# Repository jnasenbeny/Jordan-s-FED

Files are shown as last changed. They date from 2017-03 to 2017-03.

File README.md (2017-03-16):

# Jordan-s-FED
Based on the original FED from Kravitz Lab, this user-friendly device is designed to reliably dispense 45 mg rodent food pellets with minimal tinkering. A number of changes, described below, were made to the physical structure of the device. Two 'for loops' were added to the code, causing the direction of motor rotation to alternate after either 1) successful pellet dispense or 2) twelve motor steps without successful pellet dispense.  Alternating motor direction alleviates clogs in the silo.  

----------------------------------------------------------------------------------------------------------------------------------------

3D Print Design Changes from original FED are summarized as follows:

Silo:
Pellets are swept single file underneath an oval shaped wall, alleviating strain which caused clogging in the original model. Clogging is greatly reduced, increasing reliability of successful pellet dispenses and extending battery life. 

Disk:
Pellet holes widened and deepened to accomodate one 45 mg pellet at a time. 

Motor mount:
Disk tray deepened to accomodate the now taller disk.

Funnel:
Instead of dropping vertically, pellets now tumble down an ovaloid chute which sweeps laterally, reducing the chance of pellets bouncing out of the well. The new funnel piece is wider than the original and snaps into place without the use of screws.

Base:
(1) Standouts for PCB machine screws were rotated 90 degrees to make the device more user friendly. Now, the SD card is easily reached. The Power Booster lies flat on the floor and battery charging is done with the device standing upright. This increases user friendliness and slightly increases the size of the device. 
(2) Designated battery slot added to improve organization. 
(3) Switch slot was moved from the side of the device to the top, more efficiently using vertical space. 
(4) Pellet ramp was narrowed with the simple addition of walls. Pellets fall through an oval hole instead of a square one. 

Front Plate:
This component was removed from the design, since the funnel piece accomplishes the job of the old front plate. 

Lid and Back Panel:
No changes.

----------------------------------------------------------------------------------------------------------------------------------------

Performance Results:

I built 5 FEDs with these new pieces. The silos were filled completely with 45 mg pellets, and then 150 consecutive dispensing events and errors were recorded. A success counts as a single pellet landing in the well. Errors were of two types: 1) pellet bouncing out of the well; 2) two pellets dropping into the well at once. Mean success rate = 98.8%, median success rate = 98.7%.

Device 1: 
Successes -- 148/150, Errors -- bounce outs, 2.

Device 2: 
Successes -- 150/150, Errors -- none.

Device 3: 
Successes -- 149/150, Errors -- bounce out, 1.

Device 4: 
Successes -- 148/150, Errors -- bounce out, 1. double drop, 1.

Device 5:
Successes -- 148/150, Errors -- bounce out, 1. double drop, 1.

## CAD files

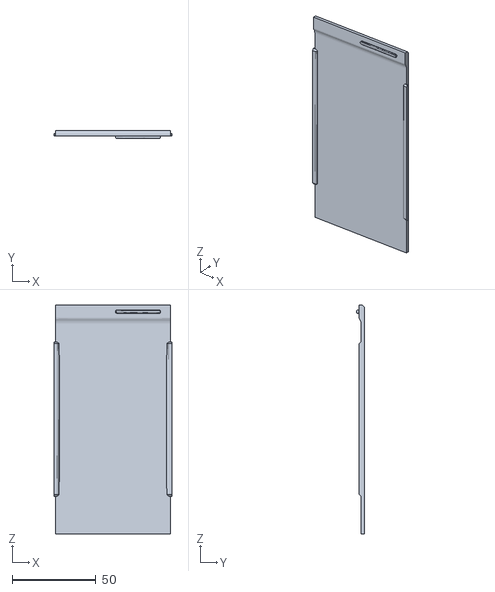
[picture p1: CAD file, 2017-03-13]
Original FED back cover.stl
70.5 x 4.75 x 137.0

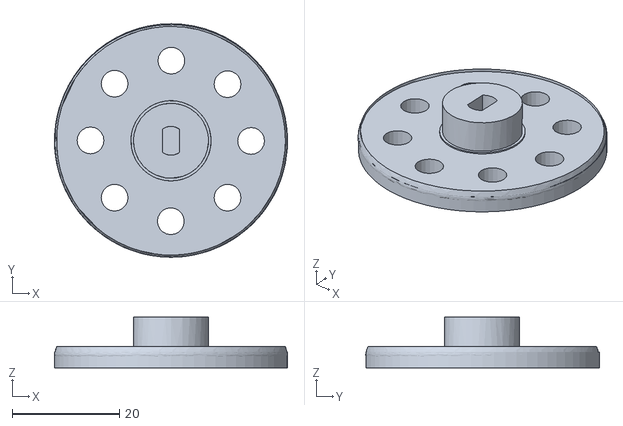
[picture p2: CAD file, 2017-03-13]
Jordan's 45 mg pellet disk.stl
43.5 x 43.6 x 9.50

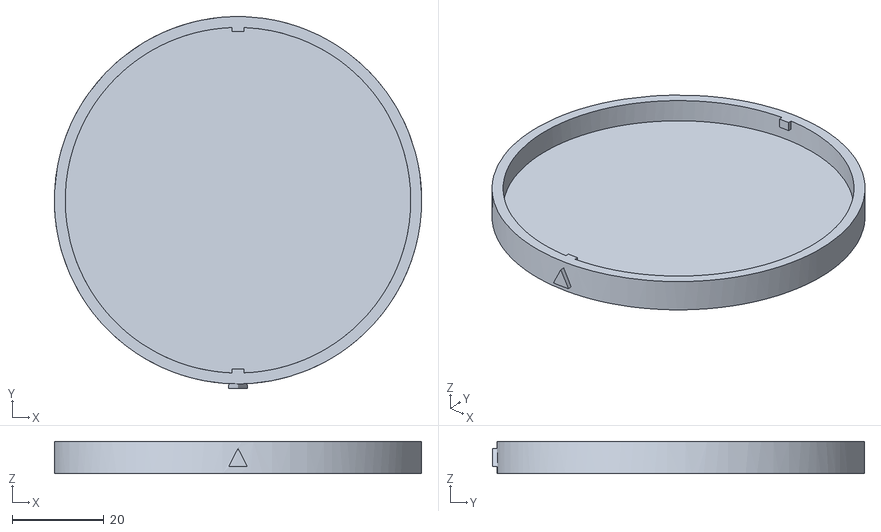
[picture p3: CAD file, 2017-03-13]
Original FED pellet hopper lid.stl
80.0 x 81.0 x 7.00

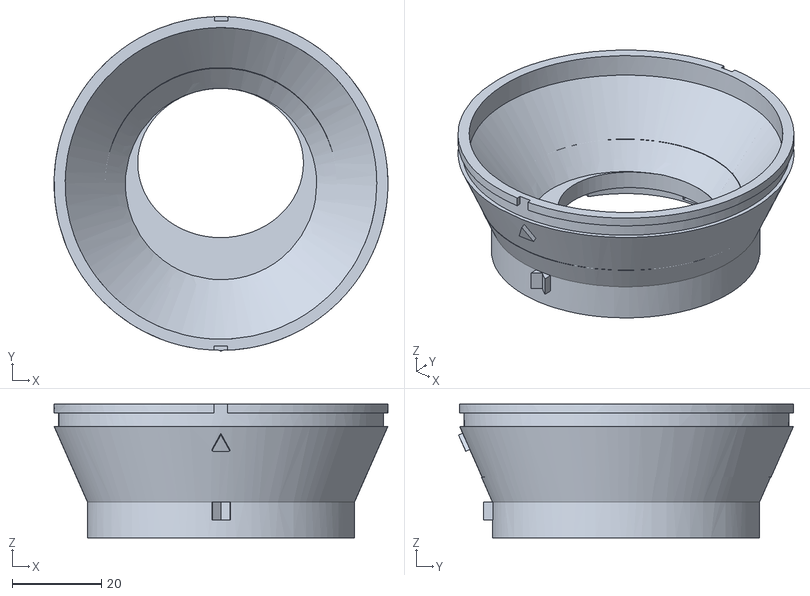
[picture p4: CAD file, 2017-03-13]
Jordan's Silo.stl
75.0 x 75.2 x 30.0

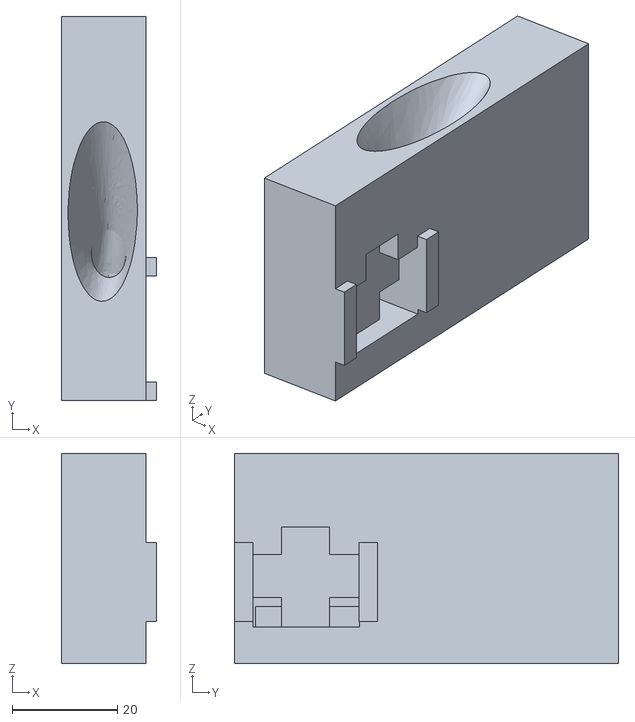
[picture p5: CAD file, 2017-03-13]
Jordan's funnel.stl
18.0 x 73.0 x 40.0

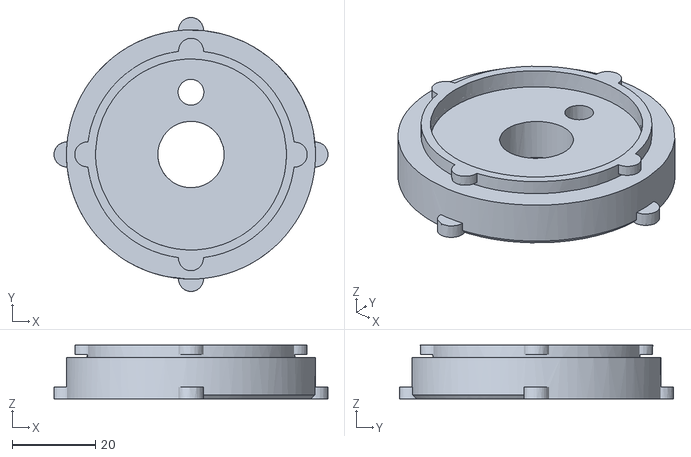
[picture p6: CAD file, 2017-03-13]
Jordan's motor mount.stl
66.0 x 66.0 x 13.0

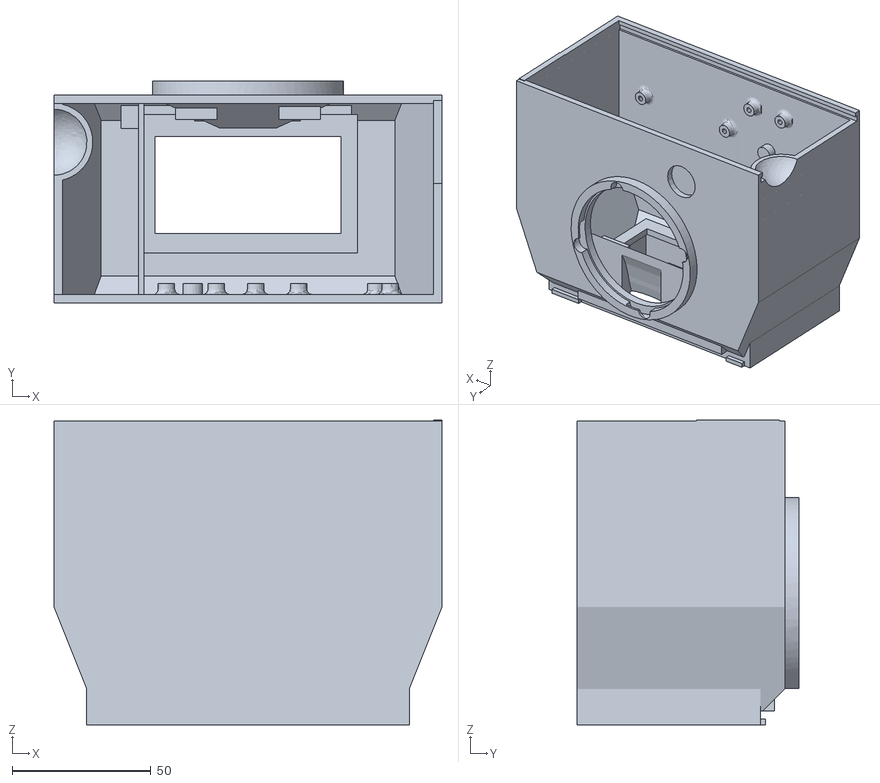
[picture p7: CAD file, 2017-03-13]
Jordan's FED Base.stl
140.0 x 80.0 x 110.0

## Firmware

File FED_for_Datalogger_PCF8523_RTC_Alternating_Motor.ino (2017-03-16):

// use this code for Arduino Data Logger Shields with PCF8523 Real Time Clock.
// Motor is set to alternate direction of rotation according to for loops in lines 168-250


#include <avr/sleep.h>
#include <avr/power.h>
#include <avr/wdt.h>
#include <SdFat.h>                // SD and RTC libraries
#include "RTClib.h"
#include <Wire.h>
#include <Stepper.h>
#include <SPI.h>
#include <Adafruit_GFX.h>
#include <Adafruit_SharpMem.h>
#include <avr/interrupt.h>
#include <avr/io.h>
#include <SoftwareSerial.h>
#include <Adafruit_MotorShield.h>



#define FILENAME "YOUR_FILENAME_HERE.csv"

#define DISPLAY_SERIAL_RX_PIN 255 // we don't need a receive pin, 255 indicates this
// Connect the Arduino pin 3 to the rx pin on the 7 segment display
#define DISPLAY_SERIAL_TX_PIN 9

// Photo interrupter is also the wakeup for the system
#define PHOTO_INTERRUPTER_PIN 2

//initialize the rtc
RTC_PCF8523 rtc;

SoftwareSerial LEDserial = SoftwareSerial(DISPLAY_SERIAL_RX_PIN, DISPLAY_SERIAL_TX_PIN);
SdFat SD;

long previousMillis = 0; 
long startTime = 0;
long timeElapsed = 0;
const long day2 = 86400000; // 86400000 milliseconds in a day
const long hour2 = 3600000; // 3600000 milliseconds in an hour
const long minute2 = 60000; // 60000 milliseconds in a minute
const long second2 =  1000; // 1000 milliseconds in a second

const int CS_pin = 10;

String time;
File dataFile;

const int TTL_DEBUG_PIN = 3;

const int STEPS_TO_INCREMENT = 65;
const int MOTOR_STEPS_PER_REVOLUTION = 513;

int PIState = 1;
int lastState = 1;

int pelletCount = 0;

// Stepper motor with shield test
Adafruit_MotorShield gMotorShield = Adafruit_MotorShield();
// Set the second argument to 1 to use M1 and M2 on the motor shield, or set as 2 to use M3 and M4:
Adafruit_StepperMotor *gPtrToStepper = gMotorShield.getStepper(MOTOR_STEPS_PER_REVOLUTION,1); 

int logData() {
  String year, month, day, hour, minute, second;
  power_twi_enable();
  power_spi_enable();

  DateTime datetime = rtc.now();
  year = String(datetime.year(), DEC);
  month = String(datetime.month(), DEC);
  day  = String(datetime.day(),  DEC);
  hour  = String(datetime.hour(),  DEC);
  minute = String(datetime.minute(), DEC);
  second = String(datetime.second(), DEC);

  // concatenates the strings defined above into date and time
  time = month + "/" + day + " " + hour + ":" + minute + ":" + second;

  // opens a file on the SD card and prints a new line with the
  // current reinforcement schedule, the time stamp,
  // the number of sucrose deliveries, the number of active and
  // inactive pokes, and the number of drinking well entries.

  dataFile = SD.open(FILENAME, FILE_WRITE);
  if (dataFile) {
    Serial.println(F("File successfully written..."));
    Serial.println(time);
    dataFile.print(time);
    dataFile.print(",");
    dataFile.print(pelletCount);
    dataFile.print(",");
    dataFile.println(timeElapsed);
    dataFile.close();
  }
  power_twi_disable();
  power_spi_disable();
}

void setup()
{

  // make all unused pins inputs with pullups enabled by default, lowest power drain
  // leave pins 0 & 1 (Arduino RX and TX) as they are
  for (byte i=2; i <= 20; i++) {    
    pinMode(i, INPUT_PULLUP);     
  }
  ADCSRA = 0;  // disable ADC as we won't be using it
  power_adc_disable(); // ADC converter
  power_timer1_disable();// Timer 1
  power_timer2_disable();// Timer 2

  Serial.begin(9600);
  Serial.println(F("Starting up..."));

  pinMode(PHOTO_INTERRUPTER_PIN, INPUT);
  pinMode(TTL_DEBUG_PIN, OUTPUT);
  pinMode(CS_pin, OUTPUT);
  pinMode(SS, OUTPUT);

  Wire.begin();
  
  // both the stepper control and RTC use I2C (the Wire library)
  rtc.begin(); // RTC library needs Wire

  // set up stepper
  gMotorShield.begin(); // use default I2C address of 0x40
  gPtrToStepper->setSpeed(30); // rpm, max suggested by Adafruit for this 5V stepper

  if (! rtc.initialized()) {
    Serial.println("RTC is NOT running!");
    // following line sets the RTC to the date & time this sketch was compiled
    rtc.adjust(DateTime(F(__DATE__), F(__TIME__)));
    // This line sets the RTC with an explicit date & time, for example to set
    // January 21, 2014 at 3am you would call:
    // rtc.adjust(DateTime(2014, 1, 21, 3, 0, 0));
  }

  if (!SD.begin(CS_pin)) {
    Serial.println(F("Card failed, or not present"));
    // don't do anything more:
    while (1) ;
  }

  Serial.println(F("Card initialized."));

  dataFile = SD.open(FILENAME, FILE_WRITE);
  if (! dataFile) {
    Serial.println(F("Error opening datalog.txt"));
    // Wait forever since we cant write data
    while (1) ;
  }

  else {
    dataFile.print(time);
    dataFile.println(F("Time,Pellet Count,Pellet Drop Delay"));
    dataFile.close();
  }
    
  delay (50);
  
  // get ready for what the system should be doing
  PIState = digitalRead(PHOTO_INTERRUPTER_PIN);
  lastState = 0;
}

void loop()
{
  int i = 0;
  int j = 0;
  
  for (i = 0; i < 12; i++){
  PIState = digitalRead(PHOTO_INTERRUPTER_PIN);
  Serial.print("Photointerrupter State: ");
  Serial.println(PIState);
  digitalWrite(TTL_DEBUG_PIN, LOW);

  if (PIState == 1  & PIState != lastState) {    
    digitalWrite(TTL_DEBUG_PIN, HIGH);    
    startTime = millis();
    Serial.print(F("Time Elapsed Check: "));
    Serial.println(timeElapsed);
    timecounter(timeElapsed);
    pelletCount ++;
    logData();
    Serial.println(F("It did work"));
    lastState = PIState;
  }
  else if (PIState == 1) {
    Serial.println(F("Turning motor..."));
    power_twi_enable();
    gPtrToStepper->step(STEPS_TO_INCREMENT/4,BACKWARD,DOUBLE);
    delay(500);
    if (PIState == 1) {gPtrToStepper->step(STEPS_TO_INCREMENT, FORWARD, DOUBLE);} 
    gPtrToStepper->release();
    power_twi_disable();
    lastState = PIState;
    delay(500);
  }
  
  else if (PIState == 0 & PIState != lastState) {
    Serial.print(F("Time Elapsed Since Last Pellet: "));
    timeElapsed = millis() - startTime;
    Serial.println(timeElapsed);
    lastState = PIState;
    break;
  }
  delay (500);
  }
    for (j = 0; j < 12; j++){
    PIState = digitalRead(PHOTO_INTERRUPTER_PIN);
  Serial.print("Photointerrupter State: ");
  Serial.println(PIState);
  digitalWrite(TTL_DEBUG_PIN, LOW);

  if (PIState == 1  & PIState != lastState) {    
    digitalWrite(TTL_DEBUG_PIN, HIGH);    
    startTime = millis();
    Serial.print(F("Time Elapsed Check: "));
    Serial.println(timeElapsed);
    timecounter(timeElapsed);
    pelletCount ++;
    logData();
    Serial.println(F("It did work"));
    lastState = PIState;
  }
  else if (PIState == 1) {
    Serial.println(F("Turning motor..."));
    power_twi_enable();
    gPtrToStepper->step(STEPS_TO_INCREMENT/4,FORWARD, DOUBLE);
    delay(500);
    if (PIState == 1) {gPtrToStepper->step(STEPS_TO_INCREMENT, BACKWARD, DOUBLE);}
    gPtrToStepper->release();
    power_twi_disable();
    lastState = PIState;
    delay(500);
  }
  
  else if (PIState == 0 & PIState != lastState) {
    Serial.print(F("Time Elapsed Since Last Pellet: "));
    timeElapsed = millis() - startTime;
    Serial.println(timeElapsed);
    lastState = PIState;
    break;
  }
    

  delay(500);
}
}
// utility function for digital clock display: prints colon and leading 0
void printDigits(byte digits) {
  if (digits < 10) {
    Serial.print('0');
  }
  Serial.print(digits, DEC);
}

void enterSleep(){
  power_usart0_disable();// Serial (USART) 

  sleep_enable();

  attachInterrupt(0, pinInterrupt, RISING);
  lastState = 0;
  delay(100);

  set_sleep_mode(SLEEP_MODE_PWR_DOWN);   /* EDIT: could also use SLEEP_MODE_PWR_DOWN for lowest power consumption. */
  cli();
  sleep_bod_disable();
  sei();
  sleep_cpu();
  sleep_disable();
}

void pinInterrupt(void){
  detachInterrupt(0);
  /* The program will continue from here after the WDT timeout*/
  sleep_disable(); /* First thing to do is disable sleep. */
  /* Re-enable the serial. */
  power_usart0_enable();
}

void timecounter(long timeNow) {
  Serial.println(timeNow);
  int days = timeNow / day2 ;                                //number of days
  int hours = (timeNow % day2) / hour2;                       //the remainder from days division (in milliseconds) divided by hours, this gives the full hours
  int minutes = ((timeNow % day2) % hour2) / minute2 ;         //and so on...
  int seconds = (((timeNow % day2) % hour2) % minute2) / second2;
  int mil = ((((timeNow % day2) % hour2) % minute2) % second2);

  // digital clock display of current time
  printDigits(hours); Serial.print(":");
  printDigits(minutes); Serial.print(":");
  printDigits(seconds); Serial.print(":");
  printDigits(mil);
  Serial.println();
}
